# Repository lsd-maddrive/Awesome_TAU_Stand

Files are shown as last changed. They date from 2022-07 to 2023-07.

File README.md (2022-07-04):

# Awesome_TAU_Stand

Проект по разработке демонстрационного стенда в помощь дисциплинам связанным с теорией управления

## Правила разработки

- Акутальная версия проекта в ветке `develop`
- Все решаемые задачи должны быть описаны в issues
- Под каждую решаемую задачу создается ветка в репозитории
- После завершения работы необходимо сделать Pull Request
- Под каждый программный модуль должен быть небольшой тест, проверяющий минимальную работоспособность
- Каждый программный модуль должен содержать комментарии, достаточные для понимания функционала и правил использования

Описание всего на свете должно быть в репозитории в виде `.md` файлов. Это могут быть ссылки на даташиты, товары в магазине, описание используемых алгоритмов, электрические схемы и т.д.

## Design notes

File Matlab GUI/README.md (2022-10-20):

## Как пользоваться Modbus TCP на STM32F767ZI.

 1) Для запуска теста нужно установить define MODBUSTCP_TEST.
 2) Подключить STM32F767ZI к компьютеру через Ethernet напрямую либо через сетевой коммутатор.
 3) Установить настройки сети как показано на изображении.
   <p align="center">
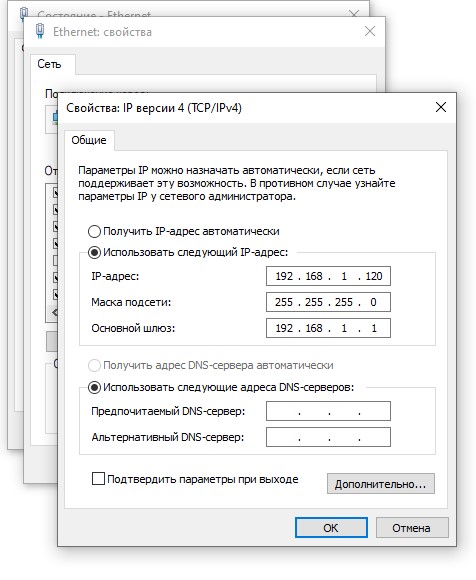
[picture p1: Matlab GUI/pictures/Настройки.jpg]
  
  </p>
  
 4) Попинговать плату, если пингуется то все подключилось. 

 5) Запустить приложение в App Designer "testgui.mlapp"
   <p align="center">
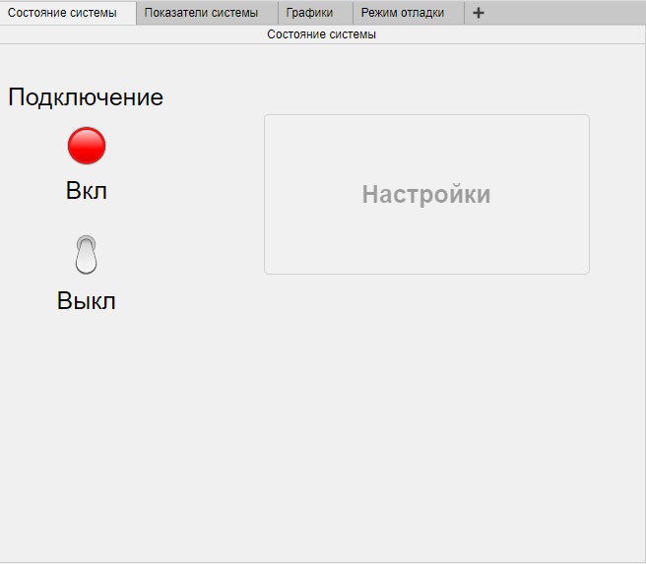
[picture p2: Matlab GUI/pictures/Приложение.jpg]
  
  </p>
  
 6) Для работы приложения необходима библиотека MODBUS для Matlab.

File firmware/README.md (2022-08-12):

# Template of Eclipse project for STM32 Nucleo144-F767ZI board with ChibiOS

### TARGET

The template runs on an STM32 Nucleo144-F767ZI board.

### Useful links

* [Reference manual (RM)](http://www.st.com/content/ccc/resource/technical/document/reference_manual/group0/96/8b/0d/ec/16/22/43/71/DM00224583/files/DM00224583.pdf/jcr:content/translations/en.DM00224583.pdf)
* [Datasheet (DS)](http://www.st.com/content/ccc/resource/technical/document/datasheet/group3/c5/37/9c/1d/a6/09/4e/1a/DM00273119/files/DM00273119.pdf/jcr:content/translations/en.DM00273119.pdf)
* [Nucleo pinout](https://os.mbed.com/platforms/ST-Nucleo-F767ZI/)
---
* [Alternate functions](http://www.st.com/content/ccc/resource/technical/document/datasheet/group3/c5/37/9c/1d/a6/09/4e/1a/DM00273119/files/DM00273119.pdf/jcr:content/translations/en.DM00273119.pdf#page=89)
* [Pins assignment (+analogs)](http://www.st.com/content/ccc/resource/technical/document/datasheet/group3/c5/37/9c/1d/a6/09/4e/1a/DM00273119/files/DM00273119.pdf/jcr:content/translations/en.DM00273119.pdf#page=65)
* [Timer triggers](http://www.st.com/content/ccc/resource/technical/document/reference_manual/group0/96/8b/0d/ec/16/22/43/71/DM00224583/files/DM00224583.pdf/jcr:content/translations/en.DM00224583.pdf#page=452)

### Notes

Based on demos from https://github.com/ChibiOS/ChibiOS

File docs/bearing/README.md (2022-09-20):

#Подшипник

Размеры: 16x8x5 мм

<p align="center">
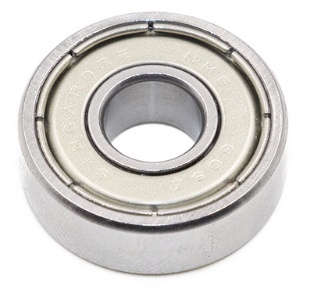
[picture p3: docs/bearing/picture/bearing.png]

</p>

[Подшипник](https://roboparts.ru/catalog/mekhanika_i_ustanovochnye_izdeliya/podshipniki/podshipnik-688zz/)

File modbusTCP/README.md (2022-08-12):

## Как пользоваться Modbus TCP на STM32F767ZI.

 1) Для запуска теста нужно установить define MODBUSTCP_TEST.
 2) Подключить STM32F767ZI к компьютеру через Ethernet напрямую либо через сетевой коммутатор.
 3) Установить настройки сети как показано на изображении.
   <p align="center">
  
  </p>
  
 4) Попинговать плату, если пингуется то все подключилось. Для проверки Modbus TCP запустить программу Modbuss Poll 
  
 [Modbuss Poll](https://www.modbustools.com/download.html)

 5) Выбрать желаемые регистры. Тут указывается адрес платы и адрес первого желаемого регистра и количество регистров на чтение.
   <p align="center">
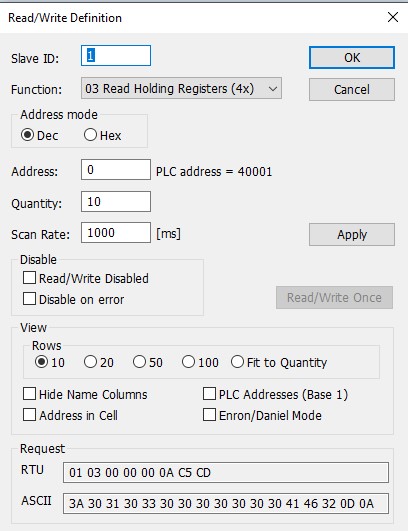
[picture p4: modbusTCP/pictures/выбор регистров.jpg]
  
  </p>
  
 6) Настроить подключение и выбрать период опроса.
   <p align="center">
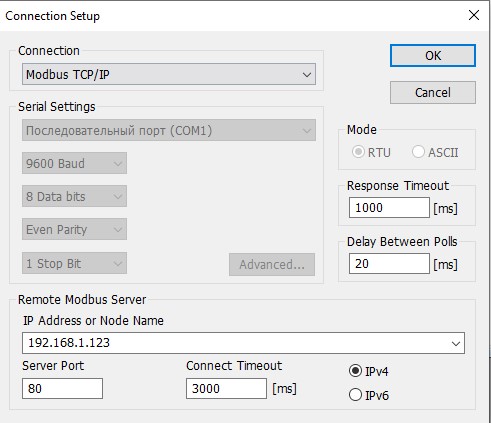
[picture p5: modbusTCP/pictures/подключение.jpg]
  
  </p>
  
 7) Если все получилось, будут отображаться регистры.
   <p align="center">
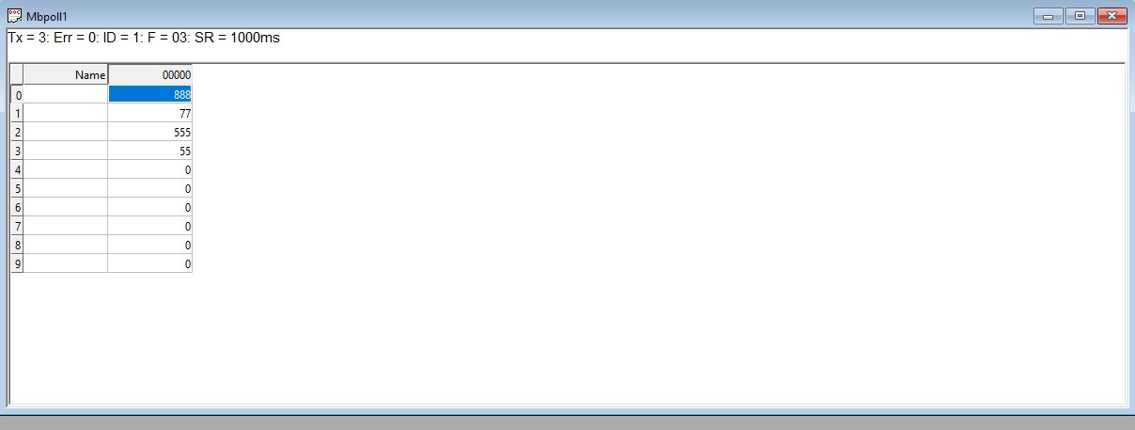
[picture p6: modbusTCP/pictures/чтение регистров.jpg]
  
  </p>
  
 8) Для изменения значения регистра нужно на него нажать и ввести желаемое значение.

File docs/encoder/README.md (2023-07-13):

#Энкодер

Модель: 6mm 5V 10bit CAN

Тип выхода: боковой выход.

Максимальная Механическая скорость: 1000 об/мин

10 бит = 1024P/R (об/мин)

Размеры: 

<p align="center">
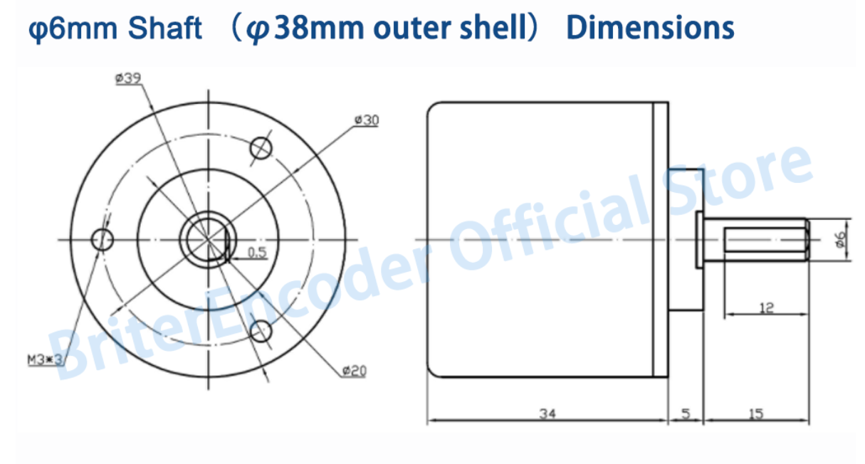
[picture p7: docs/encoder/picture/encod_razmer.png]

</p>

/*
 *  @brief  Initializes the encoder and starts another thread to read characteristics from it.
 *
 *  @note   Set encoder angular velocity sampling time (20 milliseconds).
 *  @note   Sets the zero position of the encoder.
 */
void absoluteEncoderInit(void);

/*
 *  @brief  Stops can if it's enabled.
 *
 *  @note   Not verified.
 */
msg_t absoluteEncoderUninit(void);

/*
 *  @brief  Returns rotation speed in rpm.
 *
 *  @param[out]  encoder.Speed  Encoder rotation speed in rpm.
 */
float getAbsoluteEncoderRotationalSpeed(void);

/*
 *  @brief  Returns number of turns from the starting position.
 *
 *  @param[out]  encoder.NumberOfTurns  Number of turns  can be both positive
 *                                      and negative.
 *
 */
int32_t getAbsoluteEncoderNumberOfTurns(void);

/*
 *  @brief  Returns the rotation angle of the encoder in degrees within one turn.
 *
 *  @param[out]  encoder.Angle  The rotation angle can be in the range from 0 to 360 degrees.
 */
float getAbsoluteEncoderAngleOfRotation(void);

/*
 *  @brief  Returns the rotation angle of the encoder in degrees.
 *
 *  @param[out]  encoder.Angle  The rotation angle can be greater or less than 0 degrees.
 */
int32_t getAbsoluteEncoderMultiTurnAngleOfRotation(void);

/*
 *  @brief  Returns all characteristics from the encoder.
 *
 *  @param[out]  encoder  Pointer to a structure where all characteristics are stored.
 *
 *  @note   Characteristics: rotation speed, number of turns, angle of rotation, multi-turn angle of rotation.
 */
absoluteEncoderParam* getAbsoluteEncoderStruct(void);

Команда позволяет вернуть скорость в оборотах в минуту, учитывая направление, угол поворота в градусах в диаозоне от 0 до 360 градусов,

угол в градусах, который не обнулсется после 360, количество оборотов, а также все эти данные собранные в единую структуру.

[Энкодер](https://aliexpress.ru/item/4001309275150.html?gatewayAdapt=glo2rus&sku_id=10000015687603201&spm=a2g0s.12269583.0.0.609b1e84TvdLx1)

[Энкодер datasheet](https://briterencoder.com/wp-content/uploads/2021/09/CAN-Single-Turn-User-Manual-V2.2.pdf)

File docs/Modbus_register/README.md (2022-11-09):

# Регистры Modbus

 Регистры используем для записи или чтения важных данных, уходящих или приходящих от пользователя. Так, модули с датчиками используют аналоговые регистры для хранения измерений, модули с регуляторами используют аналоговые регистры для чтения коэффициентов и для записи регулирующих воздействий.   

 Для чтения аналоговых или дискретных регистров используем define
 
 MB_READ_ANALOG_REG(addr) и MB_READ_DISCRET_REG(addr),
 
 где addr define адреса регистра(см. ниже в таблице)

 Для записи в аналоговый регистр исходя из типа данных используем define:
 
  MB_WRITE_REG_FLOAT(i,addr)
  
  MB_WRITE_REG_INT32(i,addr)
  
  MB_WRITE_REG_INT16(i,addr)
  
  где addr опять же define адреса регистра и val значение

## Аналоговые регистры

|    Имя 				         | Адрес |  Тип данных |       Модуль           | Тип взаимодействия |
|:----------------------------------------------:|:-----:|:-----------:|:----------------------:|:------------------:|
| DATA_CURRENT_SENSOR_CURRENT 	   		 |   0	 |    float    | датчик тока		|    Read only	     |
| DATA_INC_ENCODER_ROTATIONAL_SPEED		 |   2	 |    float    | инкрементальный энкодер|    Read only	     |
| DATA_ABS_ENCODER_ANGLE_OF_ROTATION		 |   4	 |    float    | абсолютный энкодер	|    Read only	     |
| DATA_ABS_ENCODER_MULTI_TURN_ANGLE_OF_ROTATION  |   6	 |    int32    | абсолютный энкодер	|    Read only	     |
| DATA_ABS_ENCODER_ROTATIONAL_SPEED		 |   8   |    float    | абсолютный энкодер	|    Read only	     |
| DATA_ABS_ENCODER_NUMBER_OF_TURNS		 |   10  |    int32    | абсолютный энкодер	|    Read only	     |
| DATA_CONTR_KP	  	  			 |   12  |    float    | регулятор		|    		     |
| DATA_CONTR_KI		  			 |   14  |    float    | регулятор		|    		     |
| DATA_CONTR_KD		  			 |   16  |    float    | регулятор		|    		     |
| DATA_CONTR_KP_2				 |   18  |    float    | регулятор		|    		     |
| DATA_CONTR_KI_2		  		 |   20  |    float    | регулятор		|    		     |
| DATA_CONTR_KD_2		  		 |   22  |    float    | регулятор		|    		     |
| DATA_CONTROL_TIME		  		 |   24  |    int16    | регулятор		|    		     |
| DATA_FORCE_PID		  		 |   26  |    float    | регулятор		|    		     |
| DATA_FORCE_KP					 |   28  |    float    | регулятор		|    		     |
| DATA_FORCE_KI					 |   30  |    float    | регулятор		|    		     |
| DATA_FORCE_KD					 |   32  |    float    | регулятор		|    		     |
| DATA_MOTOR_REQUIRED_SPEED			 |   34  |    int16    | двигатель		|    Read/Write	     |
| DATA_MOTOR_CURRENT_SPEED			 |   35  |    int16    | двигатель		|    Read only	     |
| DATA_MOTOR_REQUIRED_VOLTAGE			 |   36  |    int16    | двигатель		|    Read/Write	     |
| DATA_MOTOR_CURRENT_VOLTAGE			 |   37  |    int16    | двигатель		|    Read only	     |

## Дискретные регистры

|    Имя 				  | Адрес |
|:---------------------------------------:|:-----:|
| SYSTEM_STOP				  |   0   |
| MEASURE				  |   1	  |
| MOTOR					  |   2	  |
| FLAG_LOAD_1				  |   3	  |
| FLAG_LOAD_2				  |   4	  |	
| FLAG_LOAD_3				  |   5   |
| FLAG_CURRENT				  |   6   |
| FLAG_ABS_ENCODER			  |   7	  |	
| FLAG_INC_ENCODER			  |   8   |
| FLAG_CONTROLLER_1			  |   9   |
| FLAG_CONTROLLER_2			  |   10  |
| FLAG_VARIABLE_SPEED				  |   11  |
| FLAG_VARIABLE_ANGLE				  |   12  | 
| FLAG_VARIABLE_ROTATE  	                  	  |   13  |
| FLAG_VARIABLE_CURRENT  	                  	  |   14  |
| STATUS_MOTOR	                  	  |   15  |
| STATUS_CURRENT	                  |   16  |
| STATUS_INC_ENCODER	                  |   17  |
| STATUS_ABS_ENCODER	                  |   18  |

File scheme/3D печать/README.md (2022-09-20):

Коплект 

Ножки 14 штук

Остальные детали в одном экзепляре 

Стм - деталь для крепление стм

Датчик тока 

Драйвер

Преобразователь

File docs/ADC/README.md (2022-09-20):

#АЦП

Пороговое напряжение обычно устанавливается на уровне 2.2В c допуском примерно +-5%. Если напряжение питания будет ниже, то устройство будет находиться в состоянии сброса.

Время задержки перед включением 300мкс

Внутренный конденсатор 3.2 пФ

Рабочее напряжение: 2.7-5.5 В

Рабочая температура: -40°C-125°C

Конфиг регистра:
<p align="center">

</p>
<p align="center">
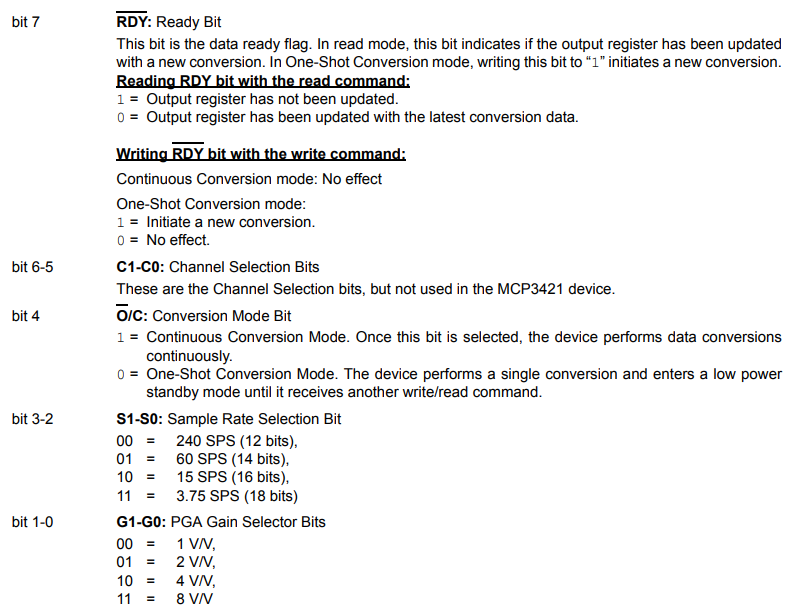
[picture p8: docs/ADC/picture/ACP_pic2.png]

</p>

Начиная с младшего бита, расположенного справа

Биты 1-0 коэф. усиления

Биты 3-2 за количество измерений в секунду или разрядность

Бит 4 отвечает за режим работы, непрерывный (все время измеряет) или по запросу (измерил и уснул)

Бит 5-6 не используется

Бит 7 закончилось ли изменение в режиме «one-shoot»

Способ передачи данных I2C:

| Кол-во бит | СколькоВ на 1 бит/коэф. усиления | измерений в сек | Min значение | Max значение |
|:----------:|:--------------------------------:|:---------------:|:------------:|:------------:|
| 12         | 1мВ                              | 240             | -2048        | 2047         |
| 14         | 250мкВ                           | 60              | -8192        | 8191         |
| 16         | 62.5мкВ                          | 15              | -32768       | 32767        |
| 18         | 15.625мкВ                        | 3.75            | -131072      | 131071       |

[АЦП](https://roboparts.ru/catalog/interfeysy_i_perekhodniki/tsap_i_atsp/gy-mcp3421/)

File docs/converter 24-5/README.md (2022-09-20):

#Преобразователь 24/5

Входное напряжение (питание) - 24 В, выходное - 5 В.

Размеры: 70x30 мм

Подключение: 

- два входа: 24В и земля

- два выхода: 5В и земля 

<p align="center">
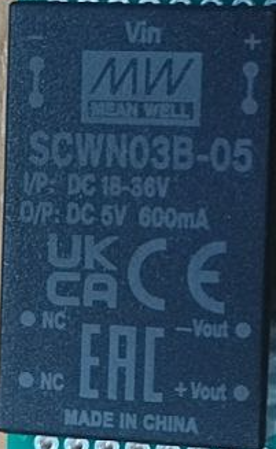
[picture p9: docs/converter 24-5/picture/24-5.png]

</p>

Рекомендуемая схема включения:

<p align="center">
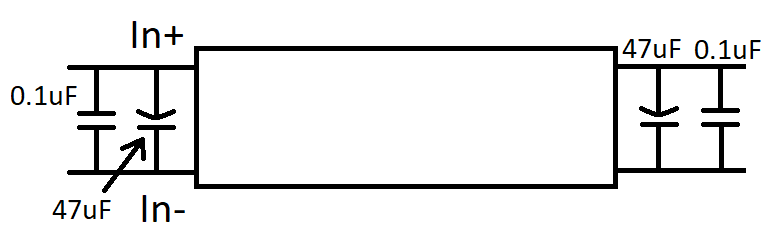
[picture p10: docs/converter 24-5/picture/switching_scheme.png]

</p>

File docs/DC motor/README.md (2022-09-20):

#36 мм Энкодер

Напряжение кодировщика составляет 5В. (Не использовать то же напряжение, что и двигатель)

Модель: 36GP-36ZYT

Модель двигателя: 2457

Точек за оборот: 500

Номинальный коэффициент уменьшения: 5.18

Номинальная допустимая нагрузка редуктора: 20

Мгновенная допустимая нагрузка редуктора (зубчатое колесо – дословный перевод): 40

Номинальная выходная мощность 23 Вт:

- Нагрузка: 2.5
- Скорость : 869 об/мин

Скорость без нагрузки: 1100 об/мин

Длина редуктора: 32.5 мм

Контрольный вес машины: 0.37 кг

Номинальный ток: 1.6А

Ток заблокированного ротора: 5А

Номинальное напряжение: 24В

Энкодер двигателя:

Напряжение питания: постоянное напряжение 5В+-10%

Максимальная частота отклика: 60 кГЦ

Максимальная скорость вращения: 1000 об/мин

Рабочая температура: -20°C~85°C

Температура хранения: -20°C~85°C

Размеры, где L=длина редуктора.

<p align="center">
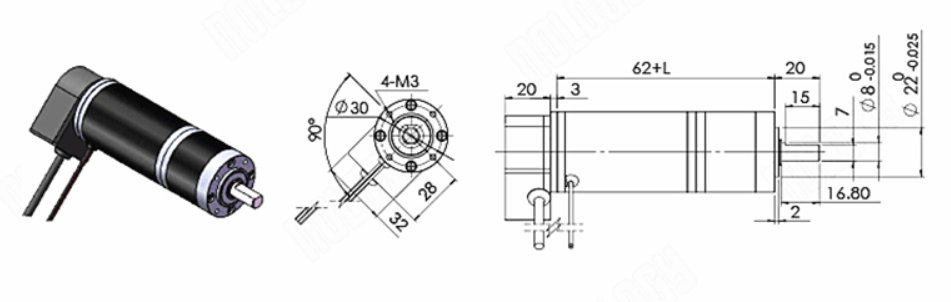
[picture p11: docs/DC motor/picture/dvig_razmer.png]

</p>

[36 мм планетарный мотор DC](https://aliexpress.ru/item/1005002059136858.html?gatewayAdapt=glo2rus&sku_id=12000018591101863&spm=a2g0s.12269583.0.0.4de131575YREKu)

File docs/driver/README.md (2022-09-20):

#Драйвер

Модель: самодельная

Размеры: 70x80 мм

Подключение: 

M-, M+ - питание двигателя

V+, V- - питание 

<p align="center">
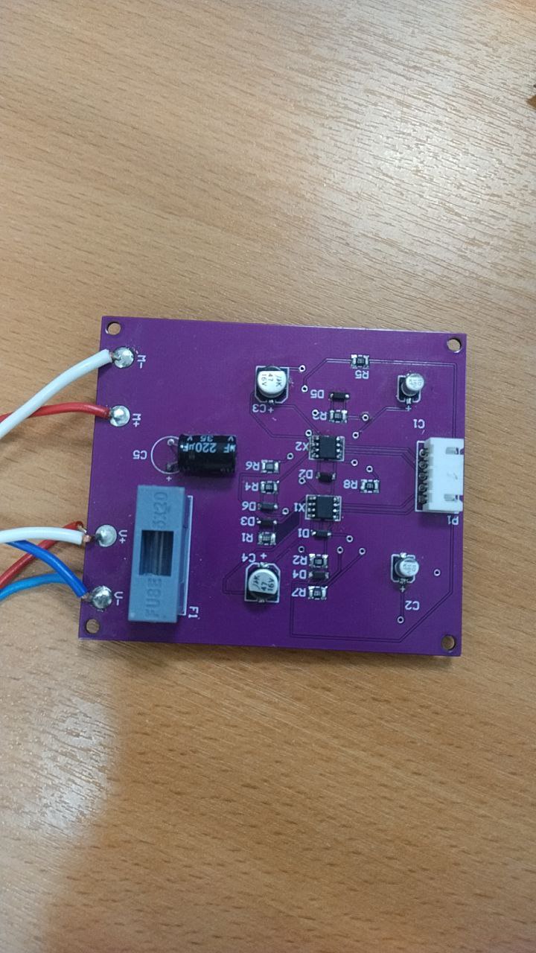
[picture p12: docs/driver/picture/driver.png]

</p>

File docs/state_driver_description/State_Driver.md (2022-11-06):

# Структура ПО нижнего уровня

В основном вся программа на микроконтроллере состоит из двух главных модулей: 

- модуль протокола Modbus
- модуль диспетчера

Modbus позволяет передавать информацию от пользователя в МК и обратно. 

Диспетчер при помощи mailbox общается с модулем Modbus и разбирает приходящую информацию, решая, что делать дальше.
И определяется это следующим образом. По mailbox диспетчер получает запрос в виде адреса ячейки Modbus и данных, которые требуются туда записать. В файле scheduler.c прописан switch-case по адресу ячеек, исходя из которых выполняются те или иные действия с записываемыми данными:  

```c
switch (address) {
      case SYSTEM_STOP:
	 ...
         break;

      case MEASURE:
	 ...
        break;
	}
	...
}
```

При этом диспетчер может переводить систему только в одно из четырёх состояний, в которых запускаются модули датчиков и регуляторов:

<p align="center">
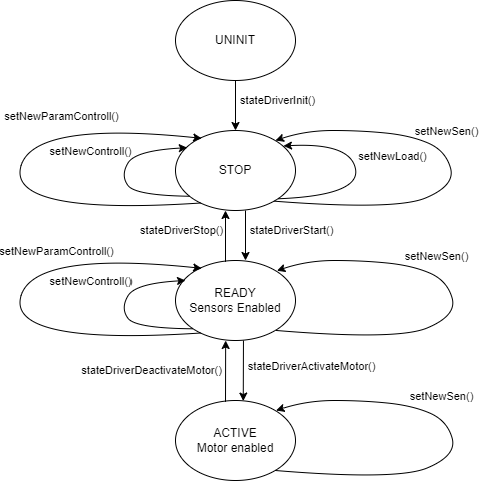
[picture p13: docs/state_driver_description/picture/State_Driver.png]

</p>

В состоянии STOP происходит выбор подключенной нагрузки, регулятора и его настроек. Тут же можно отменить включение каких-то определённых датчиков. 
  
При переходе в состояние READY  запускается поток, отвечающий за включение/выключение датчиков. Тут же можно изменить регулятор(и настройки), выбранный в предыдущем состоянии, и включит/выключить какие-то датчики
 
Далее при переходе в состояние ACTIVE происходит запуск двигателя. А также запуск потока регулятора (если он был выбран). Здесь можно менять скорость двигателя.

 Требования для модулей с датчиками:
 1)  Функции:
 
     msg_t senInit(void); (инициализирующая ф-ция должна вернуть MSG_OK при успешном включении либо MSG_RESET ) 
     
     msg_t senUninit(void);(останавливающая ф-ция должна вернуть MSG_OK при успешном выключении либо MSG_RESET ) 
     
  2)  В самих модулях использовать define записи (см. [сюда](https://github.com/lsd-maddrive/Awesome_TAU_Stand/tree/develop/docs/Modbus_register/README.md)) 
      и  define записи статуса датчика. Статус может быть:
      
	typedef enum {
	  SEN_NO_ERROR = 0,
	  SEN_BUS_ERROR = 1,
	  SEN_TIMEOUT =2,
	}senstatus_t;

Требования для модулей с регуляторами:  
  1) Функции:

     msg_t contrInit(void *arg);
  В качестве arg может передаваться некий параметр, который нужен для управления двигателем. Например, в подчинённом управлении arg - маска переменных состояния, по которым происходит регулирование.
 
      msg_t controlUninit(void);

  2) В модулях использовать define записи и чтения нужных данных из регистров Modbus

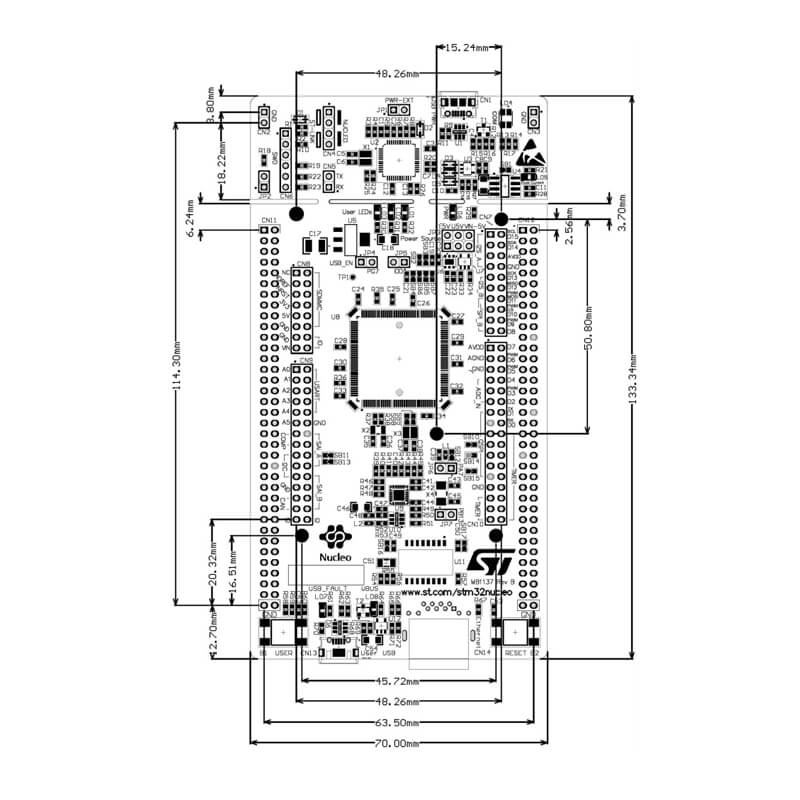
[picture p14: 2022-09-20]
docs/stm/picture/mounting_drawing.png

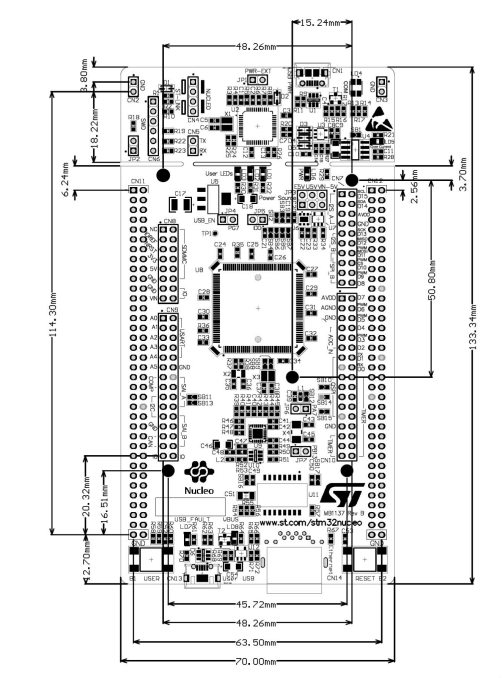
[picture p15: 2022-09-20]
docs/stm/picture/mounting_drawing2.png

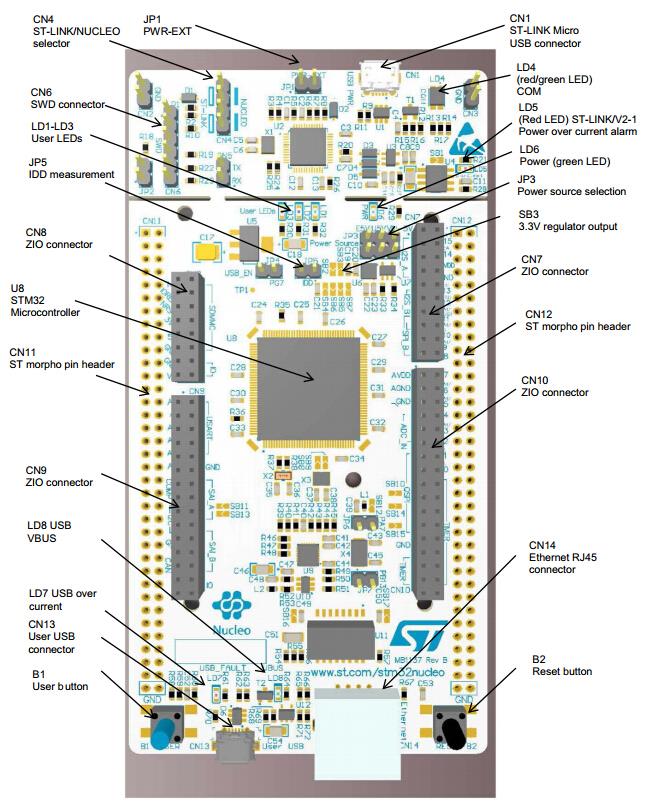
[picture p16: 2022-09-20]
docs/stm/picture/stm.png

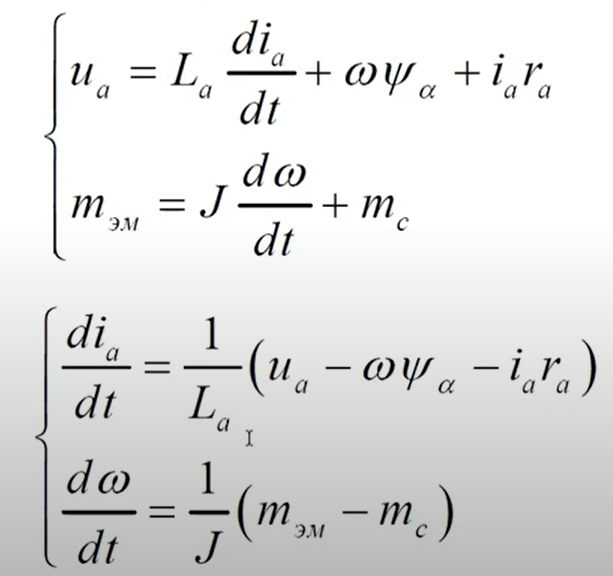
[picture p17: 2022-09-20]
docs/identification of a DC motor/picture/mathematical model.png

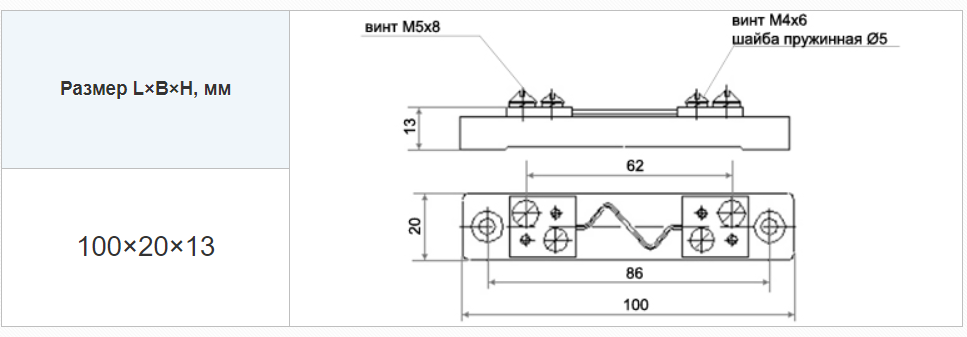
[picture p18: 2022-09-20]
docs/shunt/picture/shunt_razmer1.png

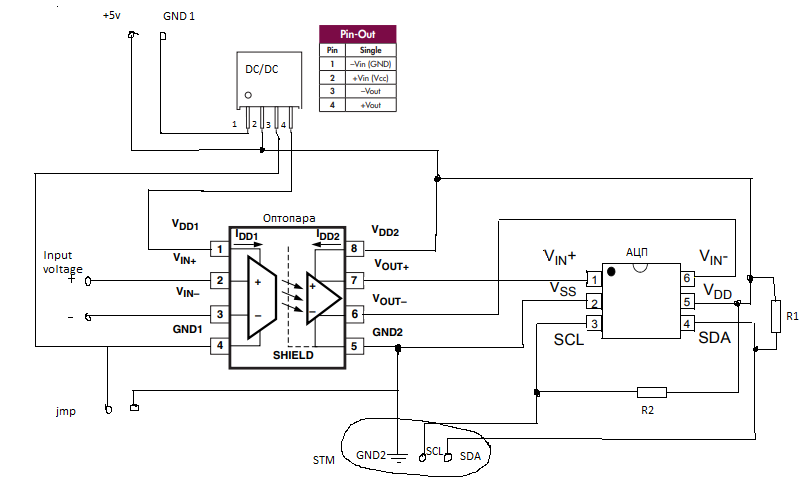
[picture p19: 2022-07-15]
docs/Current_sesor_circuit/picture/Current_sensor_circuit.png

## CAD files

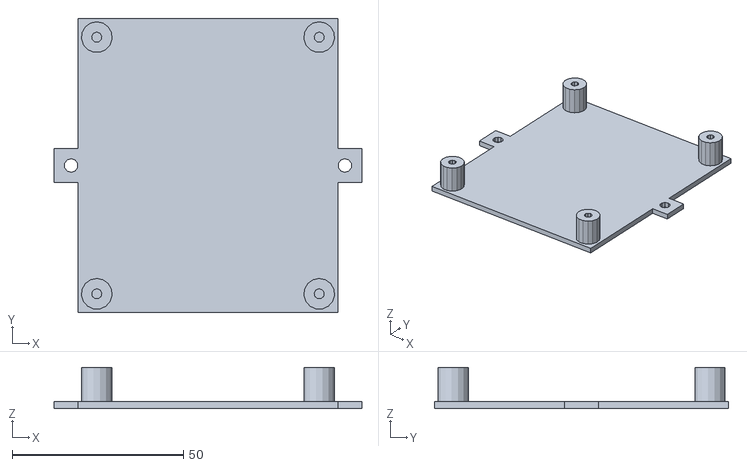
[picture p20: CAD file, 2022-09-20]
scheme/3D печать/Драйвер.stl
90.0 x 86.0 x 12.0

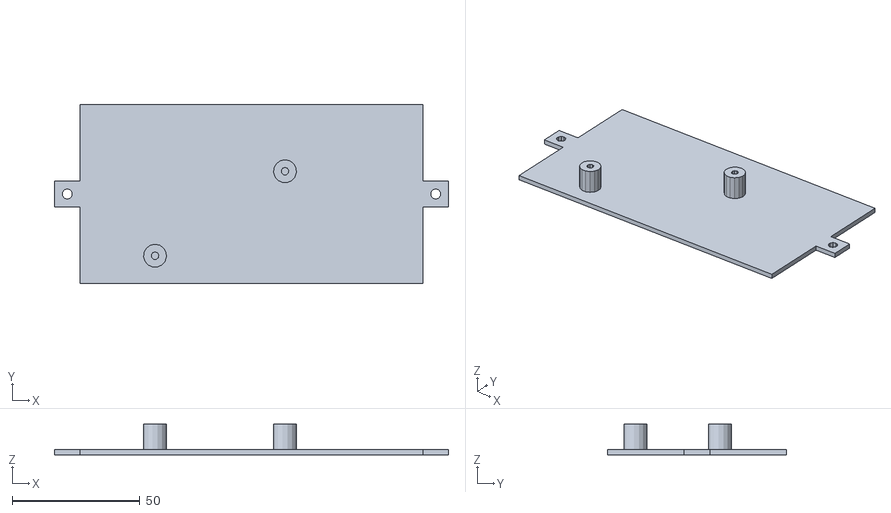
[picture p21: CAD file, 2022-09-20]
scheme/3D печать/Стм.stl
154.0 x 70.0 x 12.0

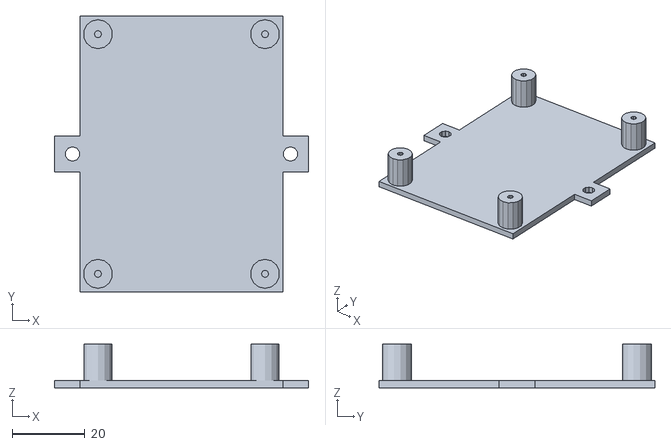
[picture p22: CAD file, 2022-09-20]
scheme/3D печать/датчик_токаm3d.stl
70.0 x 76.0 x 12.0

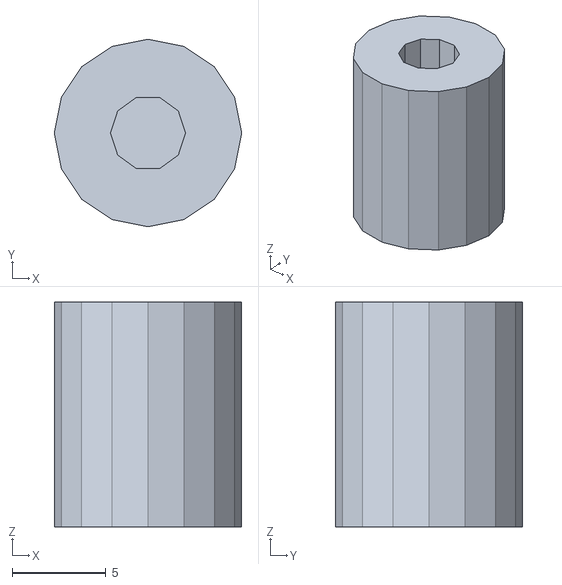
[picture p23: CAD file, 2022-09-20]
scheme/3D печать/ножка_для_платформ.stl
10.0 x 10.0 x 12.0

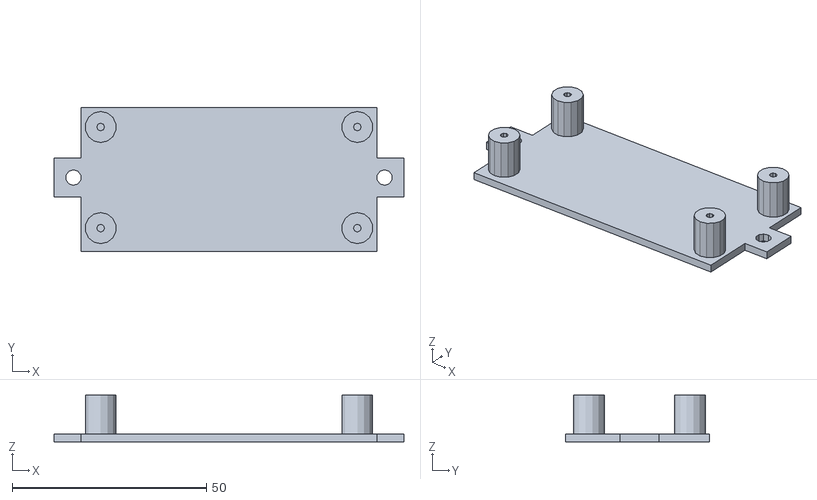
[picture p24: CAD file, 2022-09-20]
scheme/3D печать/преобразовать.stl
90.0 x 37.0 x 12.0

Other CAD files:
scheme/Деталь.dxf
scheme/Чертежи для резки/Резка_Утолщение_подшипник.dwg
scheme/чертежи для сгиба/Сгиб_Нагрузка_1.dwg
scheme/Чертежи для резки/Резка_Крепление_энкодера.dwg
scheme/чертежи для сгиба/Сгиб_Крепление_Энкодора.dwg
scheme/Чертежи для резки/Резка_Крепление_подшипника.dwg
scheme/чертежи для сгиба/Сгиб_Крепление_мотора.dwg
scheme/Чертежи для резки/Резка_Нагрузка_1.dwg
scheme/чертежи для сгиба/Сгиб_Нагрузка_2.dwg
scheme/Чертежи для резки/Резка_Крепление_мотора.dwg
scheme/чертежи для сгиба/Сгиб_Крепленеи_подшипника.dwg
scheme/Чертежи для резки/Резка_Осование_Стенда.dwg
scheme/чертежи для сгиба/Сгиба_Основание_стенда.dwg
scheme/Чертежи для резки/Резка_Нагрузка_2.dwg

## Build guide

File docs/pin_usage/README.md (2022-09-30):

# Используемые ноги на STM32.

|    Программный модуль   | Нога  | Аппаратный модуль |
|-------------------------|:-----:|:-----------------:|
|      Датчик тока        |  PB8  |    I2C1 -> SCL    |
|      Датчик тока        |  PB9  |    I2C1 -> SDA    |
|   Абсолютный энкодер    |  PD0  |    CAN1 -> RX     |
|   Абсолютный энкодер    |  PD1  |    CAN1 -> TX     |
| Инкрементальный энкодер |  PA3  |    CALLBACKS      |
| Инкрементальный энкодер |  PC0  |    CALLBACKS      |
|    Драйвер двигателя	  |  PA7  |    TIM8_CH1N      |
|    Драйвер двигателя	  |  PC6  |    TIM8_CH1       |
|    Драйвер двигателя	  |  PB0  |    TIM8_CH2N      |
|    Драйвер двигателя	  |  PC7  |    TIM8_CH2       |

Ноги для инкрементального энкодера используются для прерываний и могут быть спокойно заменены на другие.

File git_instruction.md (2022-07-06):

# Минимальный набор комманд для гита

## Клонирование репозитория

Чтобы клонировать репозиторий нужно в гите перейти в папку, где планируется хранить репозиторий. Либо с помощью `cd`:

```cd d:/chibistudio20v0/workspace```

Либо в проводнике правой кнопкой мышкой в желаемой папке `Git Bash Here`.

После этого вызываем функцию `git clone` и указываем адрес репозитория:

``` git clone https://github.com/lsd-maddrive/Awesome_TAU_Stand.git```

## Как сделать коммит

Любые локальные изменения в репозитории должны фиксироваться с помощью коммитов. Для этого нужно сначала добавить изменеия к будщему коммиту с помощью `git add`. Аргументом являются файлы изменения в которых нужно зафиксировать. Можно писать `-A`, чтобы подгрузить сразу все.

``` git add -A```

После это нужно собственно сделать коммит с помощью `git commit` Обязательным аргументом надо дать комментарий к коммиту.

``` git commit -m 'some text' ```

Перед коммитом имеет смысл проверить состояние репозитория с помощью `git status`.

## Работа с удаленным репозиторием

Для того чтобы стянуть себе актуальную версию репозитория нужно выполнить `git pull`. Чтобы залить свои изменения на удаленный репозиторий - `git push`.

*ВАЖНО!* Запушить изменения можно только в том случае, если локальный репозиторий не отстает от удаленного. То есть локально должна быть актуальная версия репозитория + некоторые изменения.

Могут возникнуть конфликты. Если локальная версия отстает от удаленного репозитория и локальные изменения затрагивают уже существующие различия, система не поймет какой из вариантов правильный. В этом случае надо будет решать конфликты руками.

## Работа с ветками

Ветку можно создать в удаленном репозитории с помощью выпадающего меню слева от названия репозитория (над этим блоком текста). По ссылке `View all branches` будет страница управления всеми ветками где можно создать новую.

Создав новую ветку надо рассказать о ней локальному репозиторию с помощью `git fetch`. После этого на нее можно переключится чтобы создать локальную версию с помощью `git checkout`:

``` git fetch
git checkout branch_name
```

Либо можно сначала создать локальную ветку с помощью того же `git checkout` с аргументом `-b`, который создаст новую ветку. После этого ее надо будет запушить в удаленный репозиторий сообщив что это новая ветка:

``` git checkout -b branch-name
делаем в ветке важные дела
git add -A
git commit -m 'comment'
git push --set-upstream origin branch-name
```

После этого между ветками можно в любой момент переключаться с помощью `git checkout`.

## Прокси

В ЛЭТИ используется прокси сервер о котором отдельно надо сообщить гиту:

``` git config --global http.proxy http://10.128.0.90:8080 ```

Чтобы прекратить использование прокси:

``` git config --global --unset http.proxy ```

# Заключение

Здесь описан самый минимум комманд для работы с гитом. Если хотите научится большему - в сети можно найти бесконечное количество различной информации в том числе на русском языке.

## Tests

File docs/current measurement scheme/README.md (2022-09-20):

# Схема измерения тока
<p align="center">
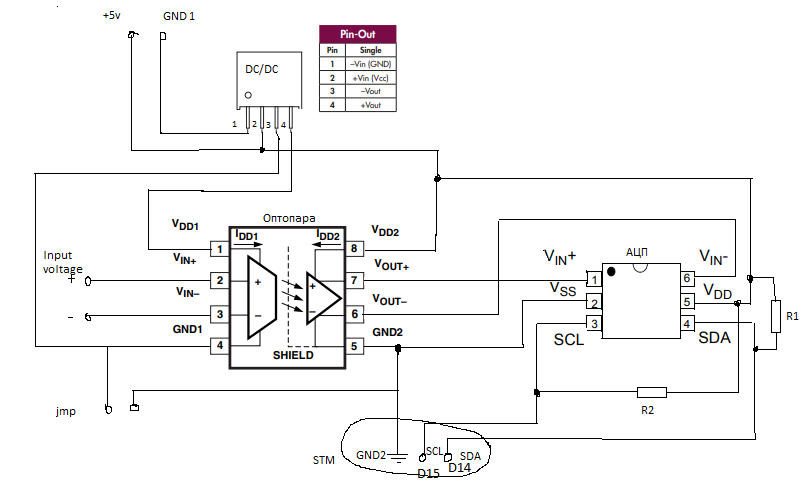
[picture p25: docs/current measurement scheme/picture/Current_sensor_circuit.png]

</p>

Косвенно измеряет ток двигателя из перерасчета напряжения

Схема состоит из трёх основных элементов: 

1) TME 0505S, DC/DC преобразователь ("DC/DC"); 

2) HCPL7840-000E, Оптопара усилитель с гальванической развязкой ("Оптопара");

3) АЦП I2C ("АЦП").

Два входных провода (+5V, GND1) приходят от преобразователя 24/5 (нет на схеме). 

Input voltage - напряжение, которое будем измерять.

jmp - джампер. Нужен для объединения/гальванической развязки земли (GND1 и GND2).

Провода GND2, SLC, SDA будут подключаться к STM.

Резисторы R1, R2 - подтягивающие резисторы. (Оставить место для них, но не припаивать)

Размер: 50x70 мм

Крепежи: ???

Ссылки на необходимую документацию:

 [DC/DC преобразователь](https://static.chipdip.ru/lib/672/DOC011672083.pdf)

 [АЦП](https://roboparts.ru/upload/iblock/77a/77a9e151265a33f9e7cf682783691282.pdf)

 [Оптопара усилитель с гальванической развязкой](https://static.chipdip.ru/lib/007/DOC013007678.pdf)

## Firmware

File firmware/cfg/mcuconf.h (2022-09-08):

/*
    ChibiOS - Copyright (C) 2006..2018 Giovanni Di Sirio

    Licensed under the Apache License, Version 2.0 (the "License");
    you may not use this file except in compliance with the License.
    You may obtain a copy of the License at

        http://www.apache.org/licenses/LICENSE-2.0

    Unless required by applicable law or agreed to in writing, software
    distributed under the License is distributed on an "AS IS" BASIS,
    WITHOUT WARRANTIES OR CONDITIONS OF ANY KIND, either express or implied.
    See the License for the specific language governing permissions and
    limitations under the License.
*/

#ifndef MCUCONF_H
#define MCUCONF_H

/*
 * STM32F7xx drivers configuration.
 * The following settings override the default settings present in
 * the various device driver implementation headers.
 * Note that the settings for each driver only have effect if the whole
 * driver is enabled in halconf.h.
 *
 * IRQ priorities:
 * 15...0       Lowest...Highest.
 *
 * DMA priorities:
 * 0...3        Lowest...Highest.
 */

#define STM32F7xx_MCUCONF
#define STM32F765_MCUCONF
#define STM32F767_MCUCONF
#define STM32F777_MCUCONF
#define STM32F769_MCUCONF
#define STM32F779_MCUCONF

/*
 * HAL driver system settings.
 */
#define STM32_NO_INIT                       FALSE
#define STM32_PVD_ENABLE                    FALSE
#define STM32_PLS                           STM32_PLS_LEV0
#define STM32_BKPRAM_ENABLE                 FALSE
#define STM32_HSI_ENABLED                   TRUE
#define STM32_LSI_ENABLED                   FALSE
#define STM32_HSE_ENABLED                   TRUE
#define STM32_LSE_ENABLED                   TRUE
#define STM32_CLOCK48_REQUIRED              TRUE
#define STM32_SW                            STM32_SW_PLL
#define STM32_PLLSRC                        STM32_PLLSRC_HSE
#define STM32_PLLM_VALUE                    8
#define STM32_PLLN_VALUE                    432
#define STM32_PLLP_VALUE                    2
#define STM32_PLLQ_VALUE                    9
#define STM32_HPRE                          STM32_HPRE_DIV1
#define STM32_PPRE1                         STM32_PPRE1_DIV4
#define STM32_PPRE2                         STM32_PPRE2_DIV2
#define STM32_RTCSEL                        STM32_RTCSEL_LSE
#define STM32_RTCPRE_VALUE                  25
#define STM32_MCO1SEL                       STM32_MCO1SEL_HSI
#define STM32_MCO1PRE                       STM32_MCO1PRE_DIV1
#define STM32_MCO2SEL                       STM32_MCO2SEL_SYSCLK
#define STM32_MCO2PRE                       STM32_MCO2PRE_DIV4
#define STM32_TIMPRE_ENABLE                 FALSE
#define STM32_I2SSRC                        STM32_I2SSRC_OFF
#define STM32_PLLI2SN_VALUE                 192
#define STM32_PLLI2SP_VALUE                 4
#define STM32_PLLI2SQ_VALUE                 4
#define STM32_PLLI2SR_VALUE                 4
#define STM32_PLLI2SDIVQ_VALUE              2
#define STM32_PLLSAIN_VALUE                 192
#define STM32_PLLSAIP_VALUE                 4
#define STM32_PLLSAIQ_VALUE                 4
#define STM32_PLLSAIR_VALUE                 4
#define STM32_PLLSAIDIVQ_VALUE              2
#define STM32_PLLSAIDIVR_VALUE              2
#define STM32_SAI1SEL                       STM32_SAI1SEL_OFF
#define STM32_SAI2SEL                       STM32_SAI2SEL_OFF
#define STM32_LCDTFT_REQUIRED               FALSE
#define STM32_USART1SEL                     STM32_USART1SEL_PCLK2
#define STM32_USART2SEL                     STM32_USART2SEL_PCLK1
#define STM32_USART3SEL                     STM32_USART3SEL_PCLK1
#define STM32_UART4SEL                      STM32_UART4SEL_PCLK1
#define STM32_UART5SEL                      STM32_UART5SEL_PCLK1
#define STM32_USART6SEL                     STM32_USART6SEL_PCLK2
#define STM32_UART7SEL                      STM32_UART7SEL_PCLK1
#define STM32_UART8SEL                      STM32_UART8SEL_PCLK1
#define STM32_I2C1SEL                       STM32_I2C1SEL_PCLK1
#define STM32_I2C2SEL                       STM32_I2C2SEL_PCLK1
#define STM32_I2C3SEL                       STM32_I2C3SEL_PCLK1
#define STM32_I2C4SEL                       STM32_I2C4SEL_PCLK1
#define STM32_LPTIM1SEL                     STM32_LPTIM1SEL_PCLK1
#define STM32_CECSEL                        STM32_CECSEL_LSE
#define STM32_CK48MSEL                      STM32_CK48MSEL_PLL
#define STM32_SDMMC1SEL                     STM32_SDMMC1SEL_PLL48CLK
#define STM32_SDMMC2SEL                     STM32_SDMMC2SEL_PLL48CLK
#define STM32_SRAM2_NOCACHE                 FALSE

/*
 * IRQ system settings.
 */
#define STM32_IRQ_EXTI0_PRIORITY            6
#define STM32_IRQ_EXTI1_PRIORITY            6
#define STM32_IRQ_EXTI2_PRIORITY            6
#define STM32_IRQ_EXTI3_PRIORITY            6
#define STM32_IRQ_EXTI4_PRIORITY            6
#define STM32_IRQ_EXTI5_9_PRIORITY          6
#define STM32_IRQ_EXTI10_15_PRIORITY        6
#define STM32_IRQ_EXTI16_PRIORITY           6
#define STM32_IRQ_EXTI17_PRIORITY           6
#define STM32_IRQ_EXTI18_PRIORITY           6
#define STM32_IRQ_EXTI19_PRIORITY           6
#define STM32_IRQ_EXTI20_PRIORITY           6
#define STM32_IRQ_EXTI21_PRIORITY           6
#define STM32_IRQ_EXTI22_PRIORITY           6
#define STM32_IRQ_EXTI23_PRIORITY           6

#define STM32_IRQ_TIM1_BRK_TIM9_PRIORITY    7
#define STM32_IRQ_TIM1_UP_TIM10_PRIORITY    7
#define STM32_IRQ_TIM1_TRGCO_TIM11_PRIORITY 7
#define STM32_IRQ_TIM1_CC_PRIORITY          7
#define STM32_IRQ_TIM2_PRIORITY             7
#define STM32_IRQ_TIM3_PRIORITY             7
#define STM32_IRQ_TIM4_PRIORITY             7
#define STM32_IRQ_TIM5_PRIORITY             7
#define STM32_IRQ_TIM6_PRIORITY             7
#define STM32_IRQ_TIM7_PRIORITY             7
#define STM32_IRQ_TIM8_BRK_TIM12_PRIORITY   7
#define STM32_IRQ_TIM8_UP_TIM13_PRIORITY    7
#define STM32_IRQ_TIM8_TRGCO_TIM14_PRIORITY 7
#define STM32_IRQ_TIM8_CC_PRIORITY          7

#define STM32_IRQ_USART1_PRIORITY           12
#define STM32_IRQ_USART2_PRIORITY           12
#define STM32_IRQ_USART3_PRIORITY           12
#define STM32_IRQ_UART4_PRIORITY            12
#define STM32_IRQ_UART5_PRIORITY            12
#define STM32_IRQ_USART6_PRIORITY           12
#define STM32_IRQ_UART7_PRIORITY            12
#define STM32_IRQ_UART8_PRIORITY            12

/*
 * ADC driver system settings.
 */
#define STM32_ADC_ADCPRE                    ADC_CCR_ADCPRE_DIV4
#define STM32_ADC_USE_ADC1                  FALSE
#define STM32_ADC_USE_ADC2                  FALSE
#define STM32_ADC_USE_ADC3                  FALSE
#define STM32_ADC_ADC1_DMA_STREAM           STM32_DMA_STREAM_ID(2, 4)
#define STM32_ADC_ADC2_DMA_STREAM           STM32_DMA_STREAM_ID(2, 2)
#define STM32_ADC_ADC3_DMA_STREAM           STM32_DMA_STREAM_ID(2, 1)
#define STM32_ADC_ADC1_DMA_PRIORITY         2
#define STM32_ADC_ADC2_DMA_PRIORITY         2
#define STM32_ADC_ADC3_DMA_PRIORITY         2
#define STM32_ADC_IRQ_PRIORITY              6
#define STM32_ADC_ADC1_DMA_IRQ_PRIORITY     6
#define STM32_ADC_ADC2_DMA_IRQ_PRIORITY     6
#define STM32_ADC_ADC3_DMA_IRQ_PRIORITY     6

/*
 * CAN driver system settings.
 */
#define STM32_CAN_USE_CAN1                  TRUE
#define STM32_CAN_USE_CAN2                  FALSE
#define STM32_CAN_USE_CAN3                  FALSE
#define STM32_CAN_CAN1_IRQ_PRIORITY         11
#define STM32_CAN_CAN2_IRQ_PRIORITY         11
#define STM32_CAN_CAN3_IRQ_PRIORITY         11

/*
 * DAC driver system settings.
 */
#define STM32_DAC_DUAL_MODE                 FALSE
#define STM32_DAC_USE_DAC1_CH1              FALSE
#define STM32_DAC_USE_DAC1_CH2              FALSE
#define STM32_DAC_DAC1_CH1_IRQ_PRIORITY     10
#define STM32_DAC_DAC1_CH2_IRQ_PRIORITY     10
#define STM32_DAC_DAC1_CH1_DMA_PRIORITY     2
#define STM32_DAC_DAC1_CH2_DMA_PRIORITY     2
#define STM32_DAC_DAC1_CH1_DMA_STREAM       STM32_DMA_STREAM_ID(1, 5)
#define STM32_DAC_DAC1_CH2_DMA_STREAM       STM32_DMA_STREAM_ID(1, 6)

/*
 * GPT driver system settings.
 */
#define STM32_GPT_USE_TIM1                  TRUE
#define STM32_GPT_USE_TIM2                  FALSE
#define STM32_GPT_USE_TIM3                  FALSE
#define STM32_GPT_USE_TIM4                  FALSE
#define STM32_GPT_USE_TIM5                  FALSE
#define STM32_GPT_USE_TIM6                  FALSE
#define STM32_GPT_USE_TIM7                  FALSE
#define STM32_GPT_USE_TIM8                  FALSE
#define STM32_GPT_USE_TIM9                  FALSE
#define STM32_GPT_USE_TIM10                 FALSE
#define STM32_GPT_USE_TIM11                 FALSE
#define STM32_GPT_USE_TIM12                 FALSE
#define STM32_GPT_USE_TIM13                 FALSE
#define STM32_GPT_USE_TIM14                 FALSE
#define STM32_GPT_USE_TIM15                 FALSE
#define STM32_GPT_USE_TIM16                 FALSE
#define STM32_GPT_USE_TIM17                 FALSE

/*
 * I2C driver system settings.
 */
#define STM32_I2C_USE_I2C1                  TRUE
#define STM32_I2C_USE_I2C2                  FALSE
#define STM32_I2C_USE_I2C3                  FALSE
#define STM32_I2C_USE_I2C4                  FALSE
#define STM32_I2C_BUSY_TIMEOUT              50
#define STM32_I2C_I2C1_RX_DMA_STREAM        STM32_DMA_STREAM_ID(1, 0)
#define STM32_I2C_I2C1_TX_DMA_STREAM        STM32_DMA_STREAM_ID(1, 7)
#define STM32_I2C_I2C2_RX_DMA_STREAM        STM32_DMA_STREAM_ID(1, 2)
#define STM32_I2C_I2C2_TX_DMA_STREAM        STM32_DMA_STREAM_ID(1, 7)
#define STM32_I2C_I2C3_RX_DMA_STREAM        STM32_DMA_STREAM_ID(1, 2)
#define STM32_I2C_I2C3_TX_DMA_STREAM        STM32_DMA_STREAM_ID(1, 4)
#define STM32_I2C_I2C4_RX_DMA_STREAM        STM32_DMA_STREAM_ID(1, 2)
#define STM32_I2C_I2C4_TX_DMA_STREAM        STM32_DMA_STREAM_ID(1, 6)
#define STM32_I2C_I2C1_IRQ_PRIORITY         5
#define STM32_I2C_I2C2_IRQ_PRIORITY         5
#define STM32_I2C_I2C3_IRQ_PRIORITY         5
#define STM32_I2C_I2C4_IRQ_PRIORITY         5
#define STM32_I2C_I2C1_DMA_PRIORITY         3
#define STM32_I2C_I2C2_DMA_PRIORITY         3
#define STM32_I2C_I2C3_DMA_PRIORITY         3
#define STM32_I2C_I2C4_DMA_PRIORITY         3
#define STM32_I2C_DMA_ERROR_HOOK(i2cp)      osalSysHalt("DMA failure")

/*
 * ICU driver system settings.
 */
#define STM32_ICU_USE_TIM1                  FALSE
#define STM32_ICU_USE_TIM2                  FALSE
#define STM32_ICU_USE_TIM3                  FALSE
#define STM32_ICU_USE_TIM4                  FALSE
#define STM32_ICU_USE_TIM5                  FALSE
#define STM32_ICU_USE_TIM8                  FALSE
#define STM32_ICU_USE_TIM9                  FALSE
#define STM32_ICU_USE_TIM10                 FALSE
#define STM32_ICU_USE_TIM11                 FALSE
#define STM32_ICU_USE_TIM12                 FALSE
#define STM32_ICU_USE_TIM13                 FALSE
#define STM32_ICU_USE_TIM14                 FALSE
#define STM32_ICU_USE_TIM15                 FALSE
#define STM32_ICU_USE_TIM16                 FALSE
#define STM32_ICU_USE_TIM17                 FALSE

/*
 * MAC driver system settings.
 */
#define STM32_MAC_TRANSMIT_BUFFERS          2
#define STM32_MAC_RECEIVE_BUFFERS           4
#define STM32_MAC_BUFFERS_SIZE              1522
#define STM32_MAC_PHY_TIMEOUT               100
#define STM32_MAC_ETH1_CHANGE_PHY_STATE     TRUE
#define STM32_MAC_ETH1_IRQ_PRIORITY         13
#define STM32_MAC_IP_CHECKSUM_OFFLOAD       0
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

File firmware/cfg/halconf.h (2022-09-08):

/*
    ChibiOS - Copyright (C) 2006..2018 Giovanni Di Sirio

    Licensed under the Apache License, Version 2.0 (the "License");
    you may not use this file except in compliance with the License.
    You may obtain a copy of the License at

        http://www.apache.org/licenses/LICENSE-2.0

    Unless required by applicable law or agreed to in writing, software
    distributed under the License is distributed on an "AS IS" BASIS,
    WITHOUT WARRANTIES OR CONDITIONS OF ANY KIND, either express or implied.
    See the License for the specific language governing permissions and
    limitations under the License.
*/

/**
 * @file    templates/halconf.h
 * @brief   HAL configuration header.
 * @details HAL configuration file, this file allows to enable or disable the
 *          various device drivers from your application. You may also use
 *          this file in order to override the device drivers default settings.
 *
 * @addtogroup HAL_CONF
 * @{
 */

#ifndef HALCONF_H
#define HALCONF_H

#define _CHIBIOS_HAL_CONF_
#define _CHIBIOS_HAL_CONF_VER_7_1_

#include "mcuconf.h"

/**
 * @brief   Enables the PAL subsystem.
 */
#if !defined(HAL_USE_PAL) || defined(__DOXYGEN__)
#define HAL_USE_PAL                         TRUE
#endif

/**
 * @brief   Enables the ADC subsystem.
 */
#if !defined(HAL_USE_ADC) || defined(__DOXYGEN__)
#define HAL_USE_ADC                         FALSE
#endif

/**
 * @brief   Enables the CAN subsystem.
 */
#if !defined(HAL_USE_CAN) || defined(__DOXYGEN__)
#define HAL_USE_CAN                         TRUE
#endif

/**
 * @brief   Enables the cryptographic subsystem.
 */
#if !defined(HAL_USE_CRY) || defined(__DOXYGEN__)
#define HAL_USE_CRY                         FALSE
#endif

/**
 * @brief   Enables the DAC subsystem.
 */
#if !defined(HAL_USE_DAC) || defined(__DOXYGEN__)
#define HAL_USE_DAC                         FALSE
#endif

/**
 * @brief   Enables the EFlash subsystem.
 */
#if !defined(HAL_USE_EFL) || defined(__DOXYGEN__)
#define HAL_USE_EFL                         FALSE
#endif

/**
 * @brief   Enables the GPT subsystem.
 */
#if !defined(HAL_USE_GPT) || defined(__DOXYGEN__)
#define HAL_USE_GPT                         TRUE
#endif

/**
 * @brief   Enables the I2C subsystem.
 */
#if !defined(HAL_USE_I2C) || defined(__DOXYGEN__)
#define HAL_USE_I2C                         TRUE
#endif

/**
 * @brief   Enables the I2S subsystem.
 */
#if !defined(HAL_USE_I2S) || defined(__DOXYGEN__)
#define HAL_USE_I2S                         FALSE
#endif

/**
 * @brief   Enables the ICU subsystem.
 */
#if !defined(HAL_USE_ICU) || defined(__DOXYGEN__)
#define HAL_USE_ICU                         FALSE
#endif

/**
 * @brief   Enables the MAC subsystem.
 */
#if !defined(HAL_USE_MAC) || defined(__DOXYGEN__)
#define HAL_USE_MAC                         TRUE
#endif

/**
 * @brief   Enables the MMC_SPI subsystem.
 */
#if !defined(HAL_USE_MMC_SPI) || defined(__DOXYGEN__)
#define HAL_USE_MMC_SPI                     FALSE
#endif

/**
 * @brief   Enables the PWM subsystem.
 */
#if !defined(HAL_USE_PWM) || defined(__DOXYGEN__)
#define HAL_USE_PWM                         TRUE
#endif

/**
 * @brief   Enables the RTC subsystem.
 */
#if !defined(HAL_USE_RTC) || defined(__DOXYGEN__)
#define HAL_USE_RTC                         FALSE
#endif

/**
 * @brief   Enables the SDC subsystem.
 */
#if !defined(HAL_USE_SDC) || defined(__DOXYGEN__)
#define HAL_USE_SDC                         FALSE
#endif

/**
 * @brief   Enables the SERIAL subsystem.
 */
#if !defined(HAL_USE_SERIAL) || defined(__DOXYGEN__)
#define HAL_USE_SERIAL                      TRUE
#endif

/**
 * @brief   Enables the SERIAL over USB subsystem.
 */
#if !defined(HAL_USE_SERIAL_USB) || defined(__DOXYGEN__)
#define HAL_USE_SERIAL_USB                  FALSE
#endif
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

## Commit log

2022-07-15 add circuit
2022-07-16 the sensor library
2022-07-21 Current sensor
2022-07-21 made new current_sensor file
2022-08-28 thread stop
2022-08-28 fix uninit thread
2022-09-06 add motor driver legs
2022-09-07 fix uninit motor
2022-09-08 create lib for motor control
2022-09-18 State driver test with connected sensor modules
2022-09-25 the functions of sensor modules have been added to the table
2022-09-25 A control module for regulators and motor start has been added to the scheduler
2022-09-29 rewrite motor test
2022-09-29 rewrite pin usage for the absolute encoder
2022-09-30 write motor test
2022-09-30 fix threads terminate
2022-09-30 added names for threads
2022-09-30 сhange function that names threads
2022-10-11 Added slave motor control
2023-07-12 fix bugs with set sensors
